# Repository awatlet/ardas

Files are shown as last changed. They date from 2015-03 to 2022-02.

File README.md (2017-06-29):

# arDAS



The arDAS project is an attempt to improve **nanoDAS** acquisition systems.

Features :
* Based on [Arduino] (http://arduino.cc/)
* 4 channels
* compatible with DAS network
* CRC control (raspardas_mode)

**Note: Don't forget to set baudrate to 57600**

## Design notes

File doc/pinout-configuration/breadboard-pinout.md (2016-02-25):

### Breadboard to Arduino pinout

#### RTC
Pin 5 of RTC(SDA) to pin 18(A4) of Arduino for I2C  
Pin 6 of RTC(SCL) to pin 19(A5) of Arduino for I2C  
Pin 7 of RTC to pin 2 of Arduino for interrupt 0  

#### Shift register 74HC595 serial to parallel
Pin 12 of shift register to pin 15 of Arduino (STCP)    
Pin 11 of shift register to pin 16 of Arduino (SHCP)    
Pin 14 of shift register to pin 14 of Arduino (DS)    

#### Counter
Pin 7 of counter to pin 5 of Arduino (RCLK) to save to registers  

#### Shift register 74HC165 parallel to serial
Pin 1 of shift register to pin 8 of Arduino (PL)     // latch pin  
Pin 2 of shift register to pin 6 of Arduino (CP)    // clock for synchronous communcation  
Pin 9 of shift register to pin 7 of Arduino (Q7)    // serial output  
Pin 15 of shift register to pin 9 of Arduino (CE)  // activation cp clock  

#### MAX232
Pin 11 of MAX232 to pin 1 of Arduino (Tx)  
Pin 12 of MAX232 to pin 0 of Arduino (Rx)  
Pin 9 of Max232 to pin 3 of Arduino (RTS)

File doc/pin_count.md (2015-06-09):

#Pins required for the ardas project

##2 pins for serial communications  
(see http://www.arduino.cc/en/Tutorial/ArduinoSoftwareRS232 and https://www.sparkfun.com/tutorials/215)  
* RX - D6  
* TX - D7  

##3 pins for RTC
* SDL - I2C
* SDA - I2C
* SQW - interrupt

##5 pins for counter 
* GAL
* GAU
* GBL
* GBU
* RCLK

##4 pins for parallel to serial shift register
* PL'
* CP
* CE
* Q7

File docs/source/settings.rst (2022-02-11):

Settings
========

The acquisition settings are given in a the python file `settings.py` that must be present in the same folder as
`raspardas.py`.

``IMPORTS``
-----------
A typical `settings.py` will start with an import section.
::

    from ardas import sensor_tools as st

``SENSORS``
-----------
The next section is a tuple of sensors objects named SENSORS.
The recommended way is to save the sensor object as a sensor####.ssr file where #### stands for the sensor id
(usually a four digit number). Then the `load_sensor` method is used to create the sensor objects.

::

    # ArDAS sensors objects connected to the ArDAS channels
    SENSORS = (st.load_sensor('0001'), st.load_sensor('0002'), st.load_sensor('0003'), st.load_sensor('0004'))

Then several dictionaries define the settings :

``DATABASE``
------------

This section gives the settings of the InfluxDB where the output of the sensors will be stored.

::

    # connexion to InfluxDB
    DATABASE = {
        'host': '*hostname.domain*',
        'port': 8086,
        'user': '*user_name*',
        'password': '*password*',
        'dbname': '*database_name*',
        'series': '*series_name*'
    }

``ARDAS``
---------

In this section the settings of the ArDAS are given.

::

    # ArDAS configuration
    ARDAS_CONFIG = {
        'station': '0001',
        'net_id': '001',
        'shield_id': '001',
        'integration_period': '0001',
        'tty': '/dev/ttyACM0',
        'raw_data_on_disk': False
    }

``MASTER``
----------

This section lists the settings used to setup a remote connection (i.e. over a telnet connection)

::

    # connection to master
    MASTER_CONFIG = {
        'local_host': '0.0.0.0',
        'local_port': *port_number*

``MESSAGES LOGGING``
--------------------

These settings control how the messages generated by raspardas.py are logged.

::

    # messages logging configuration
    LOGGING_CONFIG ={
        'debug_mode': False,
        'logging_to_console': False,
        'file_name': 'raspardas_log',
        'max_bytes': 262144,
        'backup_count': 30,
        'when': 'd',
        'interval': 1
    }

``DATA LOGGING``
----------------

These settings control how the data are logged locally.

::

    # data logging configuration
    DATA_LOGGING_CONFIG ={
        'file_name': 'data_log',
        'max_bytes': 1048576,
        'backup_count': 1024,
        'when': 'd',
        'interval': 1,
        'influxdb_logging': True
    }

``SFTP``
--------

These settings are used to define how to transfer updates of raspardas.py to the raspberry_pi (remote).

::

    # parameters to push code to raspberry via sftp_transfer.py
    SFTP = {
        'host': '*name_of_the_raspberry_pi',
        'username': '*username_for_raspberry_pi_login*',
        'password': '*password_for_raspberry_pi_login*',
        'local_path': '*path_to_local_file*',
        'remote_path': '*path_to_remote_file*'
    }

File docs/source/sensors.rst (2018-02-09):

Describe your sensors
=====================

Sensors are described in special files named `sensorXXXX.ssr` where XXXX stands for the sensor that contain `raspardas.py`.

``CALIBRATE THE SENSORS``
-------------------------
Uncalibrated FM sensors produce readings that are a frequency. You may want to calibrate your FM sensors to produce
meaningful readings in units such as °C or µm and not just Hz.

``CREATE THE .SSR FILES``
-------------------------
In the example below, four sensors are created and saved to `.ssr` files.
::

    from ardas import sensor_tools as st
    # Saves a set of sensors including its calibration in a binary '.ssr' file
    sensors = (st.FMSensor(sensor_id='0001', processing_parameters=(-16.9224032438, 0.0041525221, -1.31475837290789E-07,
                                                                2.39122208189129E-012, -1.72530800355418E-017),
                       quantity='temp.', units='°C', output_format='%6.3f', log_output=True),
           st.UncalibratedFMSensor(sensor_id='0002', log_output=False),
           st.UncalibratedFMSensor(sensor_id='0003', log_output=True),
           st.UncalibratedFMSensor(sensor_id='0004', log_output=True),
           )

    if __name__ == '__main__':
        for s in sensors:
            print(s.sensor_id + ' - ' + s.quantity + ' : ' + s.output_repr(10000))
            s.save()
        print('reload sensor...')
        s = st.load_sensor('1401')
        print(s.sensor_id + ' - ' + s.quantity + ' : ' + s.output_repr(10000) + ' Log:' + str(s.log))

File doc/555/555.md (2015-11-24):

## 555

### Pin configurations

Pin 1 - **GND**  
Pin 2 - **TRIG** 
Pin 3 - **OUT**     
Pin 4 - **RESET**    
Pin 5 - **VDD**    
Pin 6 - **DISCH**  
Pin 7 - **THRES**   
Pin 8 - **CONT**  

### How to use it

WARNING : if no pull-up on Pin 7, no square-wave ouput !!

Sensor between pin 1 and pin 2.  
Adapted resistor between pin 2 and 3.  
A pull-up resistor on pin 7(THRESHOLD) for square-wave output  
A pull-up resistor on pin 4 (RESET)  
Link pin 2(TRIG) to pin 6(DISCH)  

### Usage examples

50% duty cycle  
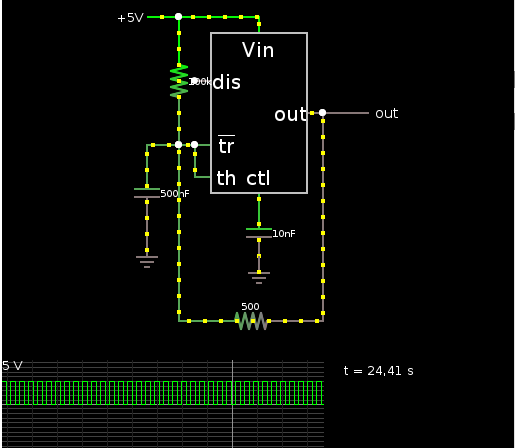
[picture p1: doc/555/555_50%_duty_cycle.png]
  

Astable A  
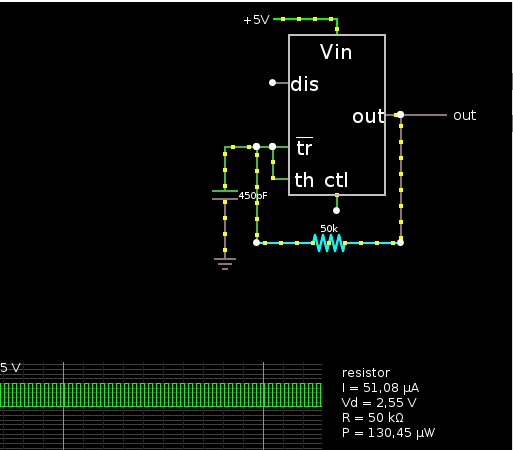
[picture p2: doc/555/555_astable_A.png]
  

Astable B  
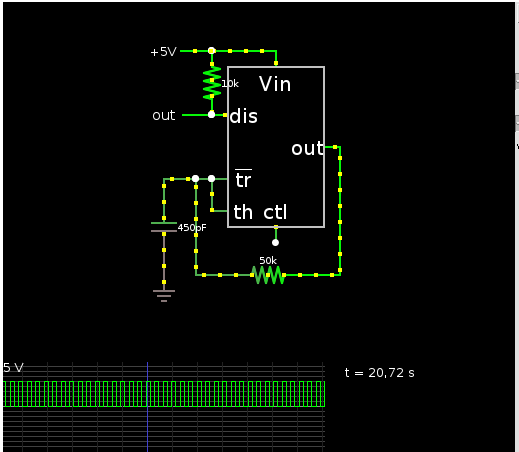
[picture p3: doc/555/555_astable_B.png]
  

Astable EDAS circuit  
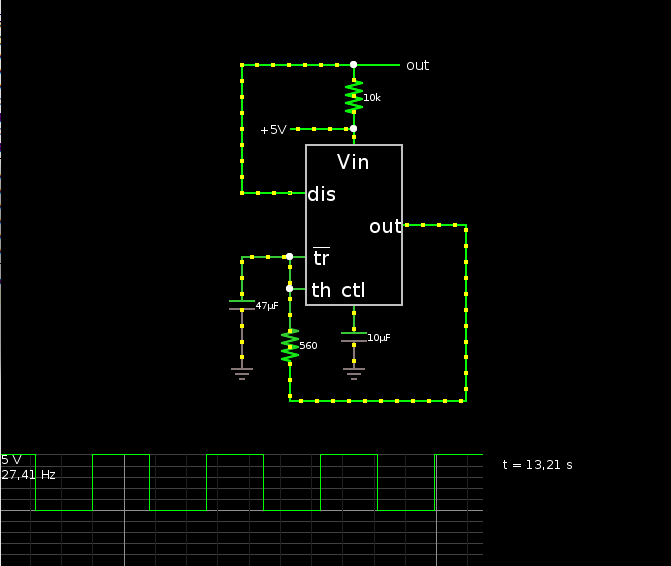
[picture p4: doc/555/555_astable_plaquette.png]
  

RC comparator    
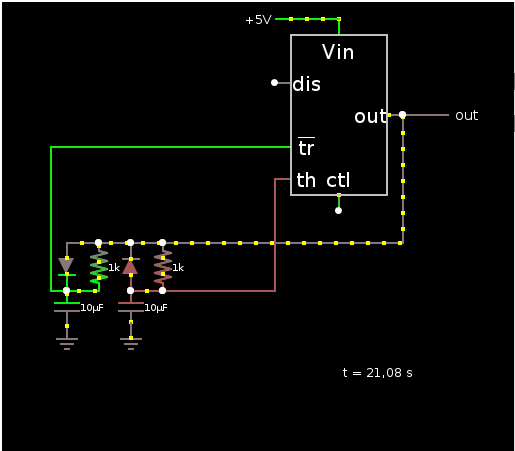
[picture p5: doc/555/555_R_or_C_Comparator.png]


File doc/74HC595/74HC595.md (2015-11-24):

## 8-bit serial-in, parallel-out shift register

### Pin configurations

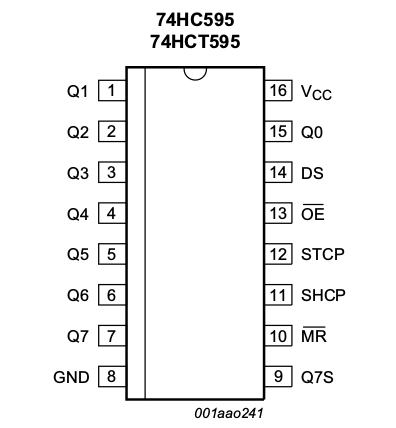
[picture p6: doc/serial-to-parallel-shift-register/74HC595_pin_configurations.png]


Pin 1 - **Q1** : parallel data output 1  
Pin 2 - **Q2** : parallel data output 2  
Pin 3 - **Q3** : parallel data output 3  
Pin 4 - **Q4** : parallel data output 4  
Pin 5 - **Q5** : parallel data output 5  
Pin 6 - **Q6** : parallel data output 6  
Pin 7 - **Q7** : parallel data output 7  
Pin 8 - **GND** :  ground  
Pin 9 - **Q7S** : serial data output  
Pin 10 - **MR** : master reset (active LOW)  
Pin 11 - **SHCP** : shift register clock input  
Pin 12 - **STCP** : storage register clock input  
Pin 13 - **OE** : output enable input (active LOW)  
Pin 14 - **DS** : serial data input  
Pin 15 - **Q0** : parallel data ouput 0  
Pin 16 - **Vcc** : supply voltage  

### How to use it

OE must be activated through pull-down resistor.  
MR must be set to HIGH through pull-up resistor.  
Pin 14 (DS) must be connected to pin 14 of Arduino (A0)  
Pin 12 (STCP) must be connected to pin 15 of Arduino (A1)  
Pin 11 (SHCP) must be connected to pin 16 of Arduino (A2)

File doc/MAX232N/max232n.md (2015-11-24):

## Dual EIA-232 driver receiver

Each receiver converts TIA/EIA-232-F inputs (RS232) to 5-V TTL/CMOS levels (Arduino Tx, Rx)  

0V to 5.5V Vcc operation  

###  Pin configurations

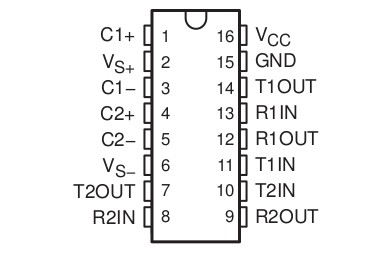
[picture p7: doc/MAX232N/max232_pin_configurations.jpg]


IN: Enter in the MAX232  
OUT: Out of the MAX232  

R: data received by the Arduino  
T: data transmit by the Arduino  

Pin 1 - **C1+**  
Pin 2 - **Vs+**  
Pin 3 - **C1-**  
Pin 4 - **C2+**  
Pin 5 - **C2-**  
Pin 6 - **Vs-**  
Pin 7 - **T2 OUT**  
Pin 8 - **R2 IN**  
Pin 9 - **R2 OUT**  
Pin 10 - **T2 IN**  
Pin 11 - **T1 IN** : data from Arduino, Tx, pin 1 (TTL)  
Pin 12 - **R1 OUT** : data to Arduino Rx, pin 0 (TTL)  
Pin 13 - **R1 IN** : data from  the PC, RxD, pin 3 on female RS232 connector (TIA/EIA-232-F)  
Pin 14 - **T1 OUT** : data to PC, TxD,  pin 2 on female RS232 connector (TIA/EIA-232-F)  
Pin 15 - **GND**  
Pin 16 - **Vcc**  

### How to use it with an Arduino

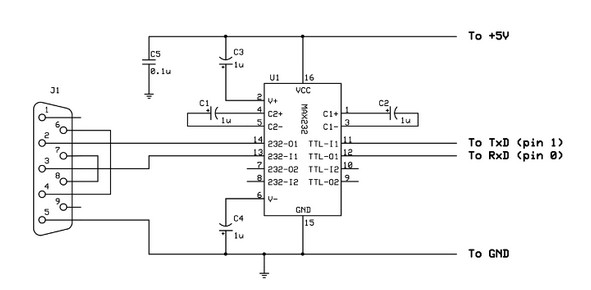
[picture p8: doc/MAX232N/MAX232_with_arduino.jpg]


Use 4 capacitors of 1uF and 1 capacitor of 0.1 uF

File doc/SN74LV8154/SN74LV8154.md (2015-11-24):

## Dual 16-BIT binary counter

2V to 5.5V Vcc operation

### Pin configurations

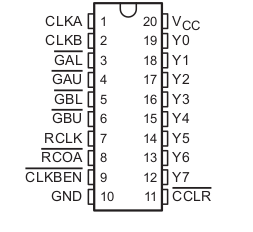
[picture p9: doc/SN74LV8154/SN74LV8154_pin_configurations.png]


Pin 1 - **CLKA** : clock for A counter  
Pin 2 - **CLKB** : clock for B counter  
Pin 3 - **GAL** : first  byte (0 to 255) for 16 bit A counter and for 32 bit AB counter   (with pull-up resitor)  
Pin 4 - **GAU** : second byte (512 to 65280) for 16 bit A counter and for 32 bit AB counter  (with pull-up resitor)  
Pin 5 - **GBL** : first byte (0 to 255) for B counter and third byte (65536 to 16711680) for 32 bit AB counter  (with pull-up resitor)   
Pin 6 - **GBU** : second byte (512 to 65280) for 16 bit B counter and fourth byte (16777216 to 4278190080) for 32 bit AB counter  (with pull-up resitor)  
Pin 7 - **RCLK** : read clock and save in storage register  
Pin 8 - **RCOA** : Output of counter A, used to realize a 32 bit counter  
Pin 9 - **CLKBEN** : input of counter B, used to realize a 32 bit counter  
Pin 10 - **GND** : Ground  
Pin 11 - **CCLR** : Clear registers  (with pull-up resitor)  
Pins 12 to 19 - **Y7 to Y0** : Ouputs  
Pin 20 - **Vcc**  

### How to use it as  two 16 bit counters

1. Connect CLKA and CLKB to GND through a pull-down resistor  
2. Connect CCLR to Vcc (pull-up)
3. Set GAL,GAU, GBL, GBU to HIGH through a pull-up resistor

### How to use it as a 32 bit counter

1. Connect RCOA to CLKBEN. Tie them to Vcc ( pull-up)
2. Connect CCLR to Vcc (pull-up)
3. Set GAL,GAU, GBL, GBU to HIGH through a pull-up resistor
4. Connect CLKA and CLKB and tie them to Vcc (pull-up)

### How to read state register

Send a positive pulse on RCLK. You can now read the outputs on Y0 to Y7.

### How to reset the counter

Send a negative pulse on CCLR.

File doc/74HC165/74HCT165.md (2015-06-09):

## 8-bit parallel-in/serial out shift register

### Pin configurations

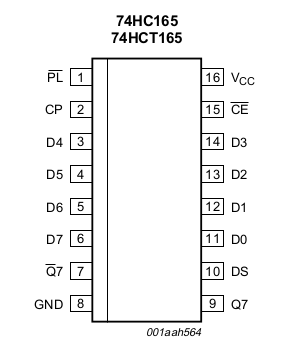
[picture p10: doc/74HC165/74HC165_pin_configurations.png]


Pin 1 - **PL** : asynchronous parallel load input (active LOW)  
Pin 2 - **CP** : clock input  
Pin 3 - **D4** : parallel data input 4    
Pin 4 - **D5** : parallel data input 5  
Pin 5 - **D6** : parallel data input 6  
Pin 6 - **D7** : parallel data input 7  
Pin 7 - **Q7** : complementary output from the last stage  
Pin 8 - **GND** :  ground    
Pin 9 - **Q7** : serial output from the last stage  
Pin 10 - **DS** : serial data input  
Pin 11 - **D0** : parallel data input 0  
Pin 12 - **D1** : parallel data input 1  
Pin 13 - **D2** : parallel data input 2  
Pin 14 - **D3** : parallel data input 3  
Pin 15 - **CE** : clock enable input (active LOW)  (with pull-down resistor)  
Pin 16 - **Vcc** : supply voltage  

### How to use it

PL is the latch pin. When it's HIGH, the shift register is listening to its 8 parallel inputs.  
When it's LOW, it is listening to the clock pin and passing information to the serial output.

CE must be activated through pull-down resistor.

The clock CP is the metronome of the conversation between the shift register and the Arduino.
Every time the Arduino sends the clock pin from LOW to HIGH, the shift register change the state
of the serial ouput pin to tell about the next switch.

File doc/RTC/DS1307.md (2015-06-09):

## I2C Real-Time Clock

### Pin configurations



Pin 1 - **X1** : Quartz  
Pin 2 - **X2** : Quartz  
Pin 3 - **VBAT** : Vcc battery  
Pin 4 - **GND** : Ground  
Pin 5 - **SDA** : Serial Data Input/Output  (with pull-up resistor)  
Pin 6 - **SCL** : Serial Clock Input  (with pull-up resistor)  
Pin 7 - **SQW/OUT** : Square Wave Output driver  (with pull-up resistor)  
Pin 8 - **VCC**  

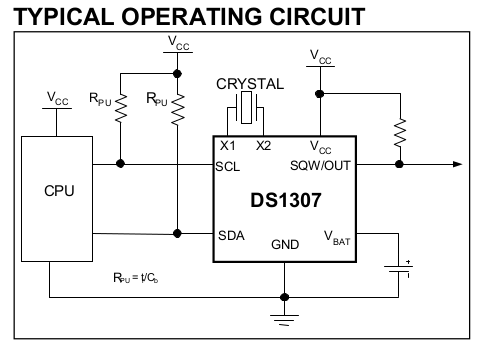
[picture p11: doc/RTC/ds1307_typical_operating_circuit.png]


### How to use it

1. Connect the Quartz on pin 1 and 2
2. Connect pin 4 of Arduino(I2C) on SDA and pin 5(I2C) to SCL
3. SDA, SCL and SQW have to be connected to Vcc through pull-up resistors (min 2k)

!IMPORTANT! : If power and backup battery are removed, the clock stops and waits to be synchronized. Square wave output doesn't work either. 
So make sure to synchronize the clock before using it !!

```
RTC.begin();
RTC.adjust(DateTime(__DATE__, __TIME__));
```

### Code example

Import RTCLib into your arduino libraries directory and launch [Square wave output example](../../examples/DS1307_sqwout.ino)

### Signal output

#### 1 Hz 
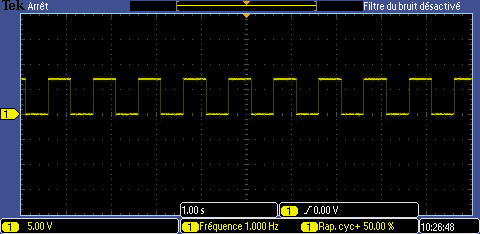
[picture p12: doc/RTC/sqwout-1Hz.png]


#### 4.096 kHz
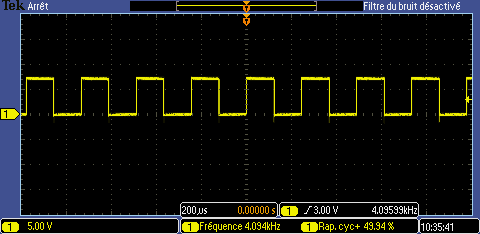
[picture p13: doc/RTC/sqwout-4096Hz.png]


#### 8.192 kHz
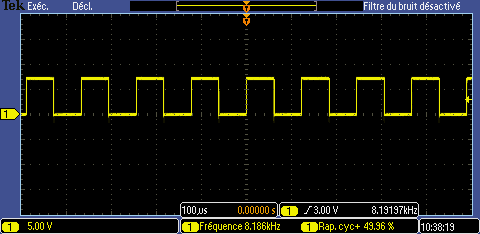
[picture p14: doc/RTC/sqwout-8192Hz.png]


#### 32.768 kHz
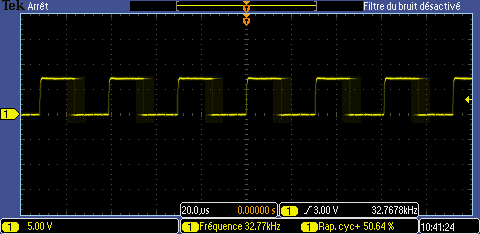
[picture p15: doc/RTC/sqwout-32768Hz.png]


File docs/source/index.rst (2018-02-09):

.. ardas documentation master file, created by
   sphinx-quickstart on Mon Mar 20 08:42:32 2017.
   You can adapt this file completely to your liking, but it should at least
   contain the root `toctree` directive.

Welcome to ardas documentation!
=================================

.. toctree::
   :maxdepth: 2
   :caption: Contents:

   getting_started
   sensors
   settings
   automatic_start_on_boot
   build_arduino_sketch
   commands

Indices and tables
==================

* :ref:`genindex`
* :ref:`modindex`
* :ref:`search`

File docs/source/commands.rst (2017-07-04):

Low level commands
==================

Raspardas uses a set of commands to communicate with the ardas.
It is possible to forward such commands through raspardas using a telnet connection using port 10001 or a direct
serial connection to the ardas is also possible but not recommended. Indeed, some of those commands are intercepted by
raspardas and processed before being forwarded to the ardas while other are only known to raspardas and have no effect
when sent directly to an ardas.

Note : Every data sequence send by an ardas is followed by \n\r (LFCR)
However each command end line sent to ardas must be \r (CR)

* -nnn : Call Das with netID nnn
* -999 : Call all Das

* #HE : Help
* #CF :
* #DG : Toggle ardas debug mode
* #E0 : No Echo
* #E1 : Only Data
* #E2 : Data + Time
* #ND : Set naïve data mode
* #RD : Set raspardas data mode
* #RC : Toggle between raw data and calibrated data
* #SD yyyy mm dd hh nn ss : Set Date
* #SR iiii : Set Integration Period
* #SI nnn : Set Das netID
* #SS ssss : Set Station Number
* #RI : Read Info
* #RV : Read version
* #ZR station netId integrationPeriod nbInst sensor1 ... code (Ex: #ZR 1111 222 3333 4 0001 0002 0003 0004 31): Reconfig
* #KL : Stop (Kill) raspardas and closes files

Some commands are no longer supported and will be removed in a future version:

* #ZF : erase memory and set default configuration
* #XB : Full Download
* #XP : yyyy mm dd hh ss yyyy mm dd hh nn ss : Partial Download
* #XS : Stop download

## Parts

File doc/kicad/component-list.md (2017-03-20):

## Component list

### Reference 

#### Arduino Uno
Microcontroller ATMEGA328P-PU ref: 1715487  http://www.farnell.com/datasheets/1684409.pdf  
DIL socket 28 ref: 2453476  

#### Ardas shield
SN74LV8154PW       X2     http://www.farnell.com/datasheets/1831074.pdf  
SN74HC595D         X1     http://www.farnell.com/datasheets/1905810.pdf  
SN74HC165D         X2     http://www.farnell.com/datasheets/1831348.pdf  
L7805CD            X1     http://www.farnell.com/datasheets/1805459.pdf  
MAX232NSR          X1     http://www.farnell.com/datasheets/1885872.pdf  
DS1307ZN+          X1     http://www.farnell.com/datasheets/46359.pdf  
Quartz ABRACON CRYSTAL, 32.768KHZ, 12.5PF  ref: 2467865  X1 http://www.farnell.com/datasheets/1883680.pdf  
Battery holder ref: 2064720  
or
Battery retainer ref: 1650692  
Arduino Shield stack header  X1 https://shop.mchobby.be/arduino/249-3-x-16-pin-header-extra-long-3232100002494.html?search_query=arduino+header&results=418

#### SD shield
HEF4050BT  ref: 1085285   x1   http://www.farnell.com/datasheets/1758120.pdf  
MICRO SD, PUSH PUSH ref:  2334075  x1 http://www.farnell.com/datasheets/1717993.pdf  

#### FM sensor
TL750L05CD  IC, V REG +5.0V  ref: 	9593659  http://www.farnell.com/datasheets/1849783.pdf  
TLC555CD  ref: 	1755233  http://www.farnell.com/datasheets/1834067.pdf  
Surface Mount Tantalum Capacitor, TAJ Series, 10 µF, ± 10%, 6.3 V  ref:1658203   
Surface Mount Thick Film Resistor, RC Series, 10 kohm, 125 mW, ± 1%  ref:	9237755  
Surface Mount Tantalum Capacitor, TAJ Series, 0.1 µF, ± 10%, 20 V  ref: 	1135082  
SMD Multilayer Ceramic Capacitor, VJ?W1BC Series, 0.01 µF, ± 10%  ref: 		2332816  

#### others
Power adaptor 9 to 12V DC, 250mA or more, 2.1mm plug, centre pin positive

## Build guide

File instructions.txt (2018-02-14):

To setup the system

1- Edit your settings
    see docs

2- Create your sensors files

3- Create a crontab task (here assuming user pi):
   PYTHONPATH=/home/pi/ardas

   # m h  dom mon dow   command
   @reboot /usr/bin/python3 /home/pi/ardas/ardas/raspardas.py > /home/pi/ardas/cronlog.log 2>&1

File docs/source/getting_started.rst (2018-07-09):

Getting started
===============

Deployment
----------

Use `ardas-tools <https://github.com/UMONS-GFA/ardas-tools>`_ scripts for easy deployment

Or deploy manually

Get the code::

    git clone https://github.com/UMONS-GFA/ardas.git

Install the requirements::

    sudo pip3 install -r requirements.txt

**Note**: numpy<=1.14 will fail to install (Original error was: **libf77blas.so.3**: cannot open shared object file: No such file or directory)

To fix this::

    sudo apt install libatlas-base-dev

Configure your settings
-----------------------

Edit the **settings_example.py** file according to your configuration and rename it settings.py.

See the `settings list parameters <settings.html>`_ for more information.

Create your sensors, you can use the script **frequency_sensor_generator.py** to generate 4 frequency sensors.

See the `sensors <sensors.html>`_ for more information.

Don't forget: for using ardas tty, the user must be in **dialout** group !

Prepare the arduino
-------------------

see `how to build arduino sketch <build_arduino_sketch.html>`_

Don't forget to set it in raspardas_mode (#RD)or with arduino_reset sketch.

Start the process
-----------------
::

    python3 raspardas.py

Stop the process
----------------

Stop the process correctly::

    telnet REMOTE_IP REMOTE_PORT

then::

    #KL

Don't forget to replace *REMOTE_PORT* by your local_port set in your settings file

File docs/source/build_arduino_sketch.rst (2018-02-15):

Build Arduino sketch
====================

Required libraries

* `Adafruit RTClib <https://github.com/adafruit/RTClib>`_ >= 1.0.0

Requirements
------------

Install required packages ::

    sudo apt-get install arduino cmake gcc-avr binutils-avr avr-libc avrdude

Fixing missing openjdk library in Debian Stretch::

    sudo mkdir /usr/lib/jvm/java-1.8.0-openjdk-armhf/jre/lib/arm/server
    sudo ln -s /usr/lib/jvm/java-8-openjdk-armhf/jre/lib/arm/client/libjvm.so /usr/lib/jvm/java-8-openjdk-armhf/jre/lib/arm/server/libjvm.so

Create a directory for your project

Put the `arduino cmake directory <https://github.com/queezythegreat/arduino-cmake>`_ inside this directory

Create a CMakeLists.txt and modify it to your needs ::

    cmake_minimum_required(VERSION 2.8)
    set(CMAKE_TOOLCHAIN_FILE ${CMAKE_SOURCE_DIR}/cmake/ArduinoToolchain.cmake)
    set(PROJECT_NAME ardas)
    project(${PROJECT_NAME})
    link_directories(${CMAKE_CURRENT_SOURCE_DIR}/libraries)
    set(${CMAKE_PROJECT_NAME}_SKETCH ardas.ino)
    generate_arduino_firmware(${CMAKE_PROJECT_NAME}
        SERIAL cutecom @SERIAL_PORT@ -b 9600 -l
        PORT  /dev/ttyACM0
        BOARD uno
    )

Build and upload to arduino board
---------------------------------

Prepare the build ::

    mkdir build
    cd build
    cmake ..

Compile ::

    make

Upload ::

    make upload

Work in Clion
-------------

Copy the .ino file inside this directory and open it with Clion

Edit the configuration

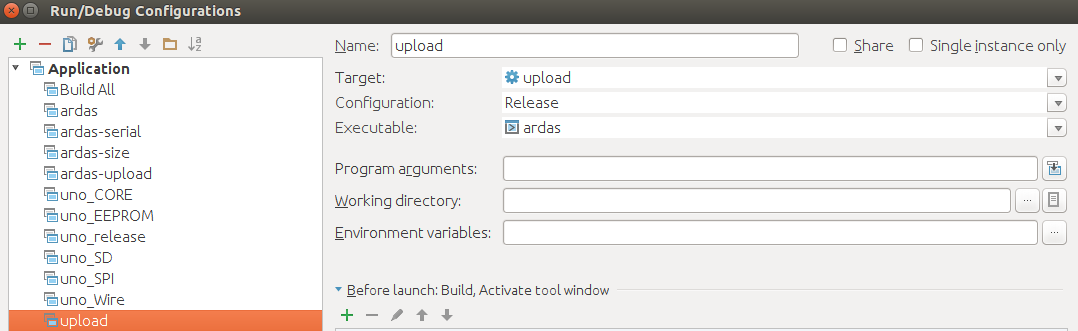
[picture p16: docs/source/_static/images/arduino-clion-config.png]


   Arduino Clion config

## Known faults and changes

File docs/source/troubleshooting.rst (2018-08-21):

Troubleshooting
===============

* Is raspardas.py running?
Check if rapsardas.py is running ::

    ps -aux | grep python3

Note processes ids (e.g. xxx)

For the low-level troubleshooting, it is necessary to kill the running instances or rapspardas.py and inter
Kill the running instances of raspardas.py ::

    kill -KILL xxx

* Does the I2C communication with RTC work?

Upload I2Cscanner in arduino ::

    cd ~/ardas/examples/i2cscanner
    mkdir build
    cd build
    cmake ..
    make
    make upload

Check output

* Does the RTC oscillate?

Upload XXX in arduino ::

    cd ~/ardas/examples/XXX
    mkdir build
    cd build
    cmake ..
    make
    make upload

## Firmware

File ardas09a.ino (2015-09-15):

/***
    Copyright (C) 2013-2015 UMONS

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
***/

#include <Wire.h>
#include <RTClib.h>
#include <EEPROM.h>
#include <SD.h>
#include <SPI.h>
#include <avr/wdt.h>

#define PULSE_WIDTH_USEC 5
#define READ_COUNTER_REGISTER_FREQ 2 // CHECK : should be 1 if freq is 1 Hz
#define CLOCK_FREQ 4096
#define VERSION "Version ARDAS 0.9a [2013-2015]"
#define EOL '\r'
#define ADDR_STATION 0
#define ADDR_NETID 2
#define ADDR_SAMPLING_RATE 3
#define ADDR_NB_INST 5
#define ADDR_I1 7
#define ADDR_I2 9
#define ADDR_I3 11
#define ADDR_I4 13

#define DATA_FILE "data.raw"

File data_file;

const uint16_t COUNTS_BETWEEN_READINGS = CLOCK_FREQ / READ_COUNTER_REGISTER_FREQ;
const uint8_t NUMBER_OF_COUNTERS = 2; // 32 bits counters
const uint8_t NUMBER_OF_CHANNELS_PER_COUNTER = 2; // 1 : 32 bits channels - 2: 16 bits channels
const uint8_t NUMBER_OF_CHANNELS = NUMBER_OF_COUNTERS * NUMBER_OF_CHANNELS_PER_COUNTER;
const uint8_t BYTES_PER_CHANNEL = 4 / NUMBER_OF_CHANNELS_PER_COUNTER;

boolean DEBUG = false; // true;
boolean quiet = true; //
uint8_t freq = CLOCK_FREQ;

RTC_DS1307 RTC;

// Pins
/* RTC */
// Don't forget to connect I2C pins A4 and A5 (5 and 6 of RTC)
// rtc_pulse on pin 2 for interrupt 0
/* SN74LV8054 */
const uint8_t rclk_pin = 5;       // set selected byte to output
/* 74HC165N */
const uint8_t pl_pin = 8;         // latch pin
const uint8_t cp_pin = 6;         // clock for synchronous communication
const uint8_t q7_pin = 7;         // serial output
const uint8_t ce_pin = 9;         // activation cp clock
/* 74HC595N */
const uint8_t stcp_pin = 15;       // pin connected to ST_CP of 74HC595
const uint8_t shcp_pin = 16;       // pin connected to SH_CP of 74HC595
const uint8_t ds_pin = 14;         // pin connected to DS of 74HC595
/* SD card */
const uint8_t ss_pin = 10;         // pin reserved for SD card output
const uint8_t cs_pin = 4;      // CS pin for SD card (4 on Ethernet shield)

//others
volatile uint16_t pulse_counter = 0;
volatile boolean read_counter_register = false;
uint32_t channel[NUMBER_OF_CHANNELS];
uint32_t c1=0;
uint32_t counter_overflow;
uint32_t previous_count[NUMBER_OF_CHANNELS];
uint32_t current_count[NUMBER_OF_CHANNELS];
uint8_t b[NUMBER_OF_COUNTERS]; // incoming bytes
uint8_t B[4]; // for reading uint32_t on SD card and reversing bit order
uint8_t cn = 0;
uint16_t n = 0;
boolean start_flag = true;
uint16_t sampling_rate = 2; // integration time in seconds
Ds1307SqwPinMode modes[] = {SquareWave1HZ, SquareWave4kHz, SquareWave8kHz, SquareWave32kHz};
Ds1307SqwPinMode RTC_freq;

// µDAS interface
uint8_t netid, nb_inst;
uint16_t station;
uint16_t inst[NUMBER_OF_CHANNELS];
uint8_t echo = 0;
boolean download_flag = false;
uint32_t p; // current position in the data_file
uint8_t record[30];

String s;

void rtc_interrupt()
{
    // after each integration period
    if (pulse_counter % COUNTS_BETWEEN_READINGS == 0){
        digitalWrite(rclk_pin, HIGH);
        digitalWrite(rclk_pin, LOW);

        read_counter_register = true;

    }
    pulse_counter ++;

}

//void(* reset) (void) = 0;//declare reset function at address 0
/* alternative possibly better one using the watchdog...
check ram usage...
#include <avr/wdt.h>
*/
void software_reset()
{
    wdt_enable(WDTO_15MS);
    while(1)
    {
    }
}

void SerialPrintf(char *format,...)
{
    char buff[80];
    va_list args;
    va_start (args,format);
    vsnprintf(buff,sizeof(buff),format,args);
    va_end (args);
    buff[sizeof(buff)/sizeof(buff[0])-1]='\0';
    Serial.print(buff);
}

void read_shift_regs()
{
    uint32_t bitVal;  // check type

    digitalWrite(ce_pin, HIGH);
    digitalWrite(pl_pin, LOW);
    delayMicroseconds(PULSE_WIDTH_USEC);
    digitalWrite(pl_pin, HIGH);
    digitalWrite(ce_pin, LOW);
    for(int j = 0; j < NUMBER_OF_COUNTERS; j++){
        b[j] = 0;
        for(int i = 0; i < 8; i++)
        {
            bitVal = (uint32_t) digitalRead(q7_pin);
            b[j] |= (bitVal << (7 - i));
            digitalWrite(cp_pin, HIGH);
            delayMicroseconds(PULSE_WIDTH_USEC);
            digitalWrite(cp_pin, LOW);
        }
    }
}

void read_bytes(uint8_t byte_number) {
    uint8_t val;

    switch(byte_number){
        case 0:
            val = 119;
            break;
        case 1:
            val = 187;
            break;
        case 2:
            val = 221;
            break;
        case 3:
            val = 238;
            break;
    }
    digitalSerialWrite(val);
    delayMicroseconds(PULSE_WIDTH_USEC);
    read_shift_regs();
    delayMicroseconds(PULSE_WIDTH_USEC);
}

void digitalSerialWrite(uint8_t Val)
{
    digitalWrite(stcp_pin, LOW);
    shiftOut(ds_pin, shcp_pin, MSBFIRST, Val);
    digitalWrite(stcp_pin, HIGH);
}

// µDAS interface
void EEPROMWriteOnTwoBytes(uint8_t address, uint8_t value) {
    uint8_t two = (value & 0xFF);
    uint8_t one = ((value >> 8) & 0xFF);

    EEPROM.write(address, two);
    EEPROM.write(address +1, one);
}

uint16_t EEPROMReadTwoBytes (uint8_t address) {
    uint8_t two = EEPROM.read (address);
    uint8_t one = EEPROM.read (address + 1);

    return ((two << 0) & 0xFF) + ((one << 8) & 0xFFFF);
}

// Get SRAM usage
int freeRam() {
    extern int __heap_start, * __brkval;
    int v;
    return (int) &v - (__brkval == 0 ? (int) &__heap_start:(int) __brkval);
}

void read_config_or_set_default() {
    station = EEPROMReadTwoBytes(ADDR_STATION);
    if (station == 0) {
        station = 1;
    }
    netid = EEPROM.read(ADDR_NETID);
    if (netid == 0) {
        netid = 255;
    }
    sampling_rate = EEPROMReadTwoBytes(ADDR_SAMPLING_RATE);
    if (sampling_rate == 0) {
        sampling_rate = 60;
    }
    nb_inst = EEPROM.read(ADDR_NB_INST);
    if ( nb_inst == 0) {
        nb_inst = NUMBER_OF_CHANNELS;
    }
}

void get_info(){
    Serial.print(F(" Station: "));
    SerialPrintf("%04d", station);
    Serial.print(F(" DasNo: "));
    SerialPrintf("%03d", netid);
    Serial.print(F(" Integration: "));
    SerialPrintf("%04d", sampling_rate);
    Serial.print(F("\n\r"));
}

void connect() {
    Serial.print(F("!HI "));
    SerialPrintf("%04d %03d %04d %1d 1111 2222 3333 4444 0 0", station, netid, sampling_rate, nb_inst); // TODO implement nb_inst!=4 + memory usage
    Serial.print(F("\n\r"));
    echo = 2;
}

void help() {
    Serial.println(F("\n\rHELP COMMAND :"));
    Serial.println(F("#E0 : No Echo"));
    Serial.println(F("#E1 : Only Data"));
    Serial.println(F("#E2 : Data + Time"));
    Serial.println(F("#SD yyyy mm dd hh nn ss : Set Date + Time"));
    Serial.println(F("#SR iiii : Set Integration Period"));
    Serial.println(F("#SS ssss : Set Station Number"));
    Serial.println(F("#SI nnn : Set DAS Number"));
    Serial.println(F("#RI : Read Info"));
    Serial.println(F("#RV : Read version"));
    Serial.println(F("#ZR ssss nnn iiii s : Reconfig"));
}

void set_no_echo() {
    Serial.println(F("\n\r!E0[Echo disabled]\n\r"));
    echo = 0;
}

void set_echo_data() {
    Serial.println(F("!E1\n\r"));
    echo = 1;
}

void set_echo_data_and_time() {
    Serial.println(F("!E2\n\r"));
    echo = 2;
}

void set_date_and_time(String s) {
    uint16_t yr;
    uint8_t mh, dy, hr, mn, sc;

    if (s.length() == 24) {
        yr = (uint16_t) s.substring(4, 8).toInt();
        mh = (uint8_t) s.substring(9, 11).toInt();
        dy = (uint8_t) s.substring(12, 14).toInt();
        hr = (uint8_t) s.substring(15, 17).toInt();
        mn = (uint8_t) s.substring(18, 20).toInt();
        sc = (uint8_t) s.substring(21, 23).toInt();
        RTC.adjust(DateTime(yr, mh, dy, hr, mn, sc));
        RTC.writeSqwPinMode(RTC_freq);
        Serial.print(F("!SD "));
        SerialPrintf("%04d %02d %02d %02d %02d %02d", yr, mh, dy, hr, mn, sc);
        Serial.print(F("\n\r"));
    }
    else {
        Serial.print(F("!SD value error\n\r"));
    }
}

void get_das_info() {
    Serial.print(F("!RI"));
    get_info();
}

void get_version() {
    Serial.print(F("!RV "));
    Serial.print(VERSION);
    Serial.print(F("\n\r"));
}


void set_station_id(String s) {
    if (s.length() == 9) {
        station = (uint16_t) s.substring(4, 8).toInt();
        EEPROMWriteOnTwoBytes(ADDR_STATION, station);
        Serial.print(F("! SS "));
        SerialPrintf("%04d", station);
        Serial.print(F("\n\r"));
    }
    else {
        Serial.print(F("!SS value error\n\r"));
    }
}

void set_das_netid(String s) {
    if(s.length() == 8) {
        netid = (uint8_t) s.substring(4,7).toInt();
        EEPROM.write(ADDR_NETID, netid);
    }
    Serial.print(F("!SI "));
    SerialPrintf("%03d",netid);
    Serial.print(F("\n\r"));
}

void set_sampling_rate(String s) {
    if (s.length() == 9) {
        // TODO: check parameter type
        sampling_rate = (uint16_t) s.substring(4,8).toInt(); // TODO unsigned int
        EEPROMWriteOnTwoBytes(ADDR_SAMPLING_RATE, sampling_rate);
        start_flag = true;
    }
    Serial.print(F("!SR "));
    SerialPrintf("%04d", sampling_rate);
    Serial.print(F("\n\r"));
}

void reconfig(String s){ // NOTE : hard coded for 4 instruments
    if (s.length() == 40) {
        station = (uint16_t) s.substring(4, 8).toInt();
        netid = (uint8_t) s.substring(9, 12).toInt();
        sampling_rate = (uint16_t) s.substring(13, 17).toInt();
        nb_inst = (uint8_t) s.substring(18, 19).toInt();
        inst[0] = (uint16_t) s.substring(20,24).toInt();
        inst[1] = (uint16_t) s.substring(25,29).toInt();
        inst[2] = (uint16_t) s.substring(30,34).toInt();
        inst[3] = (uint16_t) s.substring(35,39).toInt();


        EEPROMWriteOnTwoBytes(ADDR_STATION, station);
        EEPROM.write(ADDR_NETID, netid);
        EEPROMWriteOnTwoBytes(ADDR_SAMPLING_RATE, sampling_rate);
        EEPROM.write(ADDR_NB_INST, nb_inst);
        EEPROMWriteOnTwoBytes(ADDR_I1, inst[0]);
        EEPROM.write(ADDR_I1, inst[0]);
        EEPROMWriteOnTwoBytes(ADDR_I2, inst[1]);
        EEPROM.write(ADDR_I2, inst[1]);
        EEPROMWriteOnTwoBytes(ADDR_I3, inst[2]);
        EEPROM.write(ADDR_I3, inst[2]);
        EEPROMWriteOnTwoBytes(ADDR_I4, inst[3]);
        EEPROM.write(ADDR_I4, inst[3]);
        delay(100);
        Serial.print(F("!ZR"));
        get_info();
        start_flag = true;
    }
    else{
        Serial.print(F("!ZR value error\n\r"));
    }
}

void interrupt_download(){
    Serial.print(F("!XS\n\r"));
    download_flag = false;
}

void write_data_header(uint32_t t){
    record[0]=(uint8_t) (sampling_rate >> 8) & 0xFF;
    record[1]=(uint8_t) sampling_rate & 0xFF;
    record[2]=(uint8_t) (t >> 24) & 0xFF;
    record[3]=(uint8_t) (t >> 16) & 0xFF;
    record[4]=(uint8_t) (t >> 8) & 0xFF;
    record[5]=(uint8_t) t & 0xFF;
    for (int i=1;i<=nb_inst;i++){
        record[4+2*i]=(uint8_t) (station >> 8) & 0xFF;
        record[4+2*i+1]=(uint8_t) station & 0xFF;
    }
}
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

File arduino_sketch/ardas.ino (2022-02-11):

/*** ##### WARNING : to be used with Ardas_shield 01_2016 ##### ***/
/***
    Copyright (C) 2013-2016 UMONS

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
***/

#include <Wire.h>
#include <RTClib.h>
#include <EEPROM.h>
#include <avr/wdt.h>
#include <avr/pgmspace.h>

#define PULSE_WIDTH_USEC 5
#define READ_COUNTER_REGISTER_FREQ 4 // CHECK : should be 1 if SQW freq is 1 Hz
#define CLOCK_FREQ 4096
#define VERSION "Version ArDAS 1.0.1 [UMONS-GFA - 2016]"
#define EOL '\r'
#define ADDR_STATION 0
#define ADDR_NETID 2
#define ADDR_SAMPLING_RATE 3
#define ADDR_NB_INST 5
#define ADDR_I1 7
#define ADDR_I2 9
#define ADDR_I3 11
#define ADDR_I4 13
#define ADDR_RASPARDAS_MODE 15

#define PEER_DOWNLOAD_MODE 16
#define QUIET_MODE 17

const uint32_t PROGMEM crc_table[16] = {
    0x00000000, 0x1db71064, 0x3b6e20c8, 0x26d930ac,
    0x76dc4190, 0x6b6b51f4, 0x4db26158, 0x5005713c,
    0xedb88320, 0xf00f9344, 0xd6d6a3e8, 0xcb61b38c,
    0x9b64c2b0, 0x86d3d2d4, 0xa00ae278, 0xbdbdf21c
};

const uint16_t COUNTS_BETWEEN_READINGS = CLOCK_FREQ / READ_COUNTER_REGISTER_FREQ;
const uint8_t NUMBER_OF_COUNTERS = 2; // 32 bits counters
const uint8_t NUMBER_OF_CHANNELS_PER_COUNTER = 2; // 1 : 32 bits channels - 2: 16 bits channels
const uint8_t NUMBER_OF_CHANNELS = NUMBER_OF_COUNTERS * NUMBER_OF_CHANNELS_PER_COUNTER;
const uint8_t BYTES_PER_CHANNEL = 4 / NUMBER_OF_CHANNELS_PER_COUNTER;

boolean DEBUG = false; // true;
boolean quiet = true; //
uint8_t freq = CLOCK_FREQ;

RTC_DS1307 RTC;

// Pins
/* RTC */
// Don't forget to connect I2C pins A4 and A5 (5 and 6 of RTC)
// rtc_pulse on pin 2 for interrupt 0
/* SN74LV8054 */
const uint8_t rclk_pin = 14;       // set selected byte to output
/* 74HC165N */
const uint8_t pl_pin = 8;         // latch pin
const uint8_t cp_pin = 15;         // clock for synchronous communication
const uint8_t q7_pin = 7;         // serial output
const uint8_t ce_pin = 9;         // activation cp clock
/* 74HC595N */
const uint8_t stcp_pin = 6;       // pin connected to ST_CP of 74HC595
const uint8_t shcp_pin = 3;       // pin connected to SH_CP of 74HC595
const uint8_t ds_pin = 5;         // pin connected to DS of 74HC595


//others
volatile uint16_t pulse_counter = 0;
volatile boolean read_counter_register = false;
uint32_t channel[NUMBER_OF_CHANNELS];
uint32_t c1=0;
uint32_t counter_overflow;
uint32_t previous_count[NUMBER_OF_CHANNELS];
uint32_t current_count[NUMBER_OF_CHANNELS];
uint8_t b[NUMBER_OF_COUNTERS]; // incoming bytes
uint8_t cn = 0;
uint16_t n = 0;
boolean start_flag = true;
boolean peer_download = false;
boolean raspardas_mode = false;
uint8_t nfe = 0;
uint16_t sampling_rate = 2; // integration time in seconds
Ds1307SqwPinMode modes[] = {SquareWave1HZ, SquareWave4kHz, SquareWave8kHz, SquareWave32kHz};
Ds1307SqwPinMode RTC_freq;

// µDAS interface
uint8_t netid, nb_inst;
uint16_t station;
uint16_t inst[NUMBER_OF_CHANNELS];
uint8_t echo = 0;
boolean download_flag = false;
uint8_t record[33];
uint8_t crc[4];
uint32_t dc[NUMBER_OF_CHANNELS];
uint32_t fc[NUMBER_OF_CHANNELS];


String s;

void rtc_interrupt()
{
    //noInterrupts(); // TODO : check if needed
    // after each integration period
    if (pulse_counter % COUNTS_BETWEEN_READINGS == 0){
        digitalWrite(rclk_pin, HIGH);
        digitalWrite(rclk_pin, LOW);

        read_counter_register = true;

    }
    pulse_counter ++;
    //interrupts(); // TODO : check if needed
}

//void(* reset) (void) = 0;//declare reset function at address 0
/* alternative possibly better one using the watchdog...
check ram usage...
*/
void software_reset()
{
    wdt_enable(WDTO_15MS);
    while(1)
    {
    }
}

uint32_t crc_update(uint32_t crc, byte data)
{
    byte tbl_idx;
    tbl_idx = crc ^ (data >> (0 * 4));
    crc = pgm_read_dword_near(crc_table + (tbl_idx & 0x0f)) ^ (crc >> 4);
    tbl_idx = crc ^ (data >> (1 * 4));
    crc = pgm_read_dword_near(crc_table + (tbl_idx & 0x0f)) ^ (crc >> 4);
    return crc;
}

uint32_t crc_string(char *msg, size_t arraySize)
{
  uint32_t crc = ~0L;
  for (int i=0; i < arraySize; i++) {
    crc = crc_update(crc, *msg++);
  }
  crc = ~crc;
  return crc;
}
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

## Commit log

2014-04-22 change commands to lower case
2015-03-10 add pin configuration and typical operating circuit
2015-03-10 add counter pin configurations
2015-03-17 add pin configurations image
2015-03-26 add pin configurations
2015-05-15 added RTC_SD_RS232_shield design in Fritzing
    [RTC_SD_RS232_shield.fzz]
2015-06-24 add 555 circuits examples
2015-08-31 test writing data on SD card - warning this code could be freezing arduino...
2015-10-06 add RTS pin for Max232
2016-02-17 Changed PIN layout for ArDAS Shield
2016-02-25 add arduino-clion-config
2016-02-26 changed LED coding
2017-03-03 add calibration file example
2017-03-07 rename arduino folder
2017-03-19 added the start_sequence function to set the ardas up (station, net_id and integration period hard_coded for the time beeing) fix should be included in the new config file that will replace the calib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
2017-03-20 add arduino building doc
2018-01-05 Calibration functions inserted in settings.py
2018-01-08 v1.1.2.38 Replaced calibration by sensor objects - Implemented a Rotating raspardas.log file
2018-01-10 v1.1.2.39 - Startup doesn't work properly - but implemented a rotating logging based on time and size with compression + a little bit of cleaning codes - fixing some bugs in sensor_tools
2018-02-09 v1.1.3.2 - Implemented 'series' name settings ands updated sensor tag to include net_id
2018-02-13 getting git branch and current version to describe software version - see issue #84
2018-02-13 added instructions, .gitignore and sensors creation example
2018-02-14 start developing sampler.py
2018-02-15 optimized fake sensor generation
2018-02-15 W1 sensor response interpolation to fixed time intervals
2018-02-15 added a queue to the sampler class
2018-02-15 updated the sampler class to switch to FakeTempSensor if w1thermsensor cannot be imported
2018-02-16 rebased the sensor classes and their use in sampler
2018-02-16 add get_available_sensors for real 1W sensors
2018-02-16 Introduced SensorConditioner classes
2018-02-16 Improved SensorConditioner classes
2018-02-17 changed sensor_id by id
2018-02-17 testing sampler
2018-02-17 Working sampler for W1Thermsensors and FakeTempSensors
2018-03-02 renamed sensorsconditioners as samplesconditioners, added logger and channels_loggers
2018-03-02 reworked code to name things according to this workflow:
    sensor --sampler--> sample --conditioner--> record --logger--> log
    records_loggers not developed yet!
2018-03-02 reworked code to name things according to this workflow:
    some small fixes added
    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
2018-07-05 add frequency sensor generator
2018-07-05 update doc to generate sensors
2018-07-09 add doc to prepare arduino
2018-10-17 add script to generate uncalibrated sensors
2018-11-09 don't lauch master threads if start sequence return 1
2019-01-22 fix sensor generator sensor type
2019-09-25 Renamed folders and file to avoid error message with Arduino IDE 2:1.05+dfsg2-4.1

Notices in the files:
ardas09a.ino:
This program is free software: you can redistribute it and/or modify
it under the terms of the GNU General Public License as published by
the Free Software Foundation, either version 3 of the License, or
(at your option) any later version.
